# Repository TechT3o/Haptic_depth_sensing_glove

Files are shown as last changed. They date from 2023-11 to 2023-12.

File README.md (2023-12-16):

# Haptic_depth_sensing_glove

Haptic feedback glove device that uses a motor camera and mini motor disks to help visually impaired people understand the 3d space around them.

The idea is to mount a small camera on the palm of the visually impaired user, construct the depth map, and perform sensory substitution of vision by using a high-resolution haptic feedback glove comprised of an array of vibrational mini DC motor disks to assign a different intensity in the direction where the user's hand is pointing at, analogous to how close the object is.

The goal is for the user to be able to identify what type of object their hand is pointing at for object recognition and object fetching and for the user to be able to do wayfinding and navigate in a room using the device.

User studies that examine the usability (Learnability, Efficiency, Memorability, Errors, Satisfaction) and effectiveness of the device will be done.

# Hardware

- 1x [ESP32](https://www.espressif.com/en/products/socs/esp32)
- 1x [OV5640 camera module](https://www.amazon.com/Cameras-2592X1944-Industrial-Windows-Raspberry/dp/B088RD74VC?th=1)
- 20x [Mini motor disk](https://www.adafruit.com/product/1201#technical-details)
- 20x [p2n222A npn transistor](https://www.onsemi.com/pdf/datasheet/p2n2222a-d.pdf)
- 20x 30 Ohms resistor
- 20x 2.2k Ohms resistor
- 20x 33 pF capacitor
- 20x 1N4001 diode
- 20x [motor circuit PCB](https://github.com/TechT3o/Haptic_depth_sensing_glove/tree/main/PCB%20files)

## Motor driver circuit

The mini disk motors require around 100 mA of current in order to rotate at full speed with 5V power. The Arduino output pins can provide up to 10 mA, therefore we need a driver circuit to be able to power the motor using a PWM signal. The circuit shown in Figure 1 was built. It uses an NPN transistor whose base is connected to the GPIO output pin of the Arduino. When the PWM signal gets applied to the base of the transistor the Collector Emitter channel opens and current from the VCC flows through the disk motor and makes it spin with intensity analogous to the PWM signal. The resistor R2 limits the current flowing through the disk motor. A value of 30 Ohms was selected as 5V/30 = 166 mA max current that could flow through R2 ignoring rest of the circuit resistances. R1 was selected to limit the base current. As the base current is very small values of up to 5k could be selected but the chosen value for R1 in this project was 2.2k Ohms. The capacitor is used to soften voltage spikes from the power supply and suppress electrical noise from the motor's rotation and a diode is put to protect against back EMF.



*Figure 1: Motor driver circuit*

The PCB of this circuit shown in Figure 2 was made and the Gerber files were sent to [OSHPARK](https://oshpark.com/) for manufacturing.



*Figure 2: Motor driver PCB*

The received PCBs arrived and the components were soldered on top of it with the disk motors attached to the back of the PCB.



*Figure 3: PCB*



*Figure 4: Soldered circuits and motor coordinates*

## Camera

When choosing the camera we wanted a camera with a small size that could fit the device, as little distortion as possible (no wide angle cameras that tend to have a lot of barrel distortion), low latency and good enough resolution for the depth estimation model to give accurate results. The camera selected was a 5MP USB Camera Webcam with 60 Degree FOV and Autofocus Lens by IFWATER.

It used the OV5640 CMOS (Complementary Metal-Oxide-Semiconductor) image sensor which has high resolution of 2592 x 1944 pixels and can achieve frame rates of 30 FPS.

The location of the camera was another dilemma in our design consideration. As originally intended, it was supposed to be connected to the user's body. However, by relocating the camera to the palm, we eliminated the need to determine the depth relative to the hand, thereby simplifying the entire system. Placing the camera on the palm allows for a more natural interaction with the environment.

## Microcontroller
The microcontroller picked is an ESP32 DevkitC module. It was selected because it is affordable, has the options of wireless connectivity and low power consumption and unlike the Arduino Nano 33 BLE Sense which was the first attempt has no upper limit into how many GPIO pins can provide a PWM signal concurrently. 



*Figure 5: ESP32 module*

## Depth Estimation

In order to estimate the depth from a mono camera the vision transformer model DPT-Large by Intel was used. This transformer was trained on 1.4 million images for monocular depth estimation and it can predict the relative depth in an image frame. The Python class [MonoDepthEstimator](https://github.com/TechT3o/Haptic_depth_sensing_glove/blob/main/depth_estimation.py) implements this transformer with functions that can find the depth of a frame. For sanity checking the depth frames are visualized as a 3D point cloud using the [3D reconstruction](https://github.com/TechT3o/Haptic_depth_sensing_glove/blob/main/3d_reconstruct.py) script and the relative distances between the objects captured seem reasonable and is accurate for which object is closer to the camera. A sample depth video that is used to test the glove in its early stages and to visualize the depth estimation created by the [depth video creating script](https://github.com/TechT3o/Haptic_depth_sensing_glove/blob/main/depth_video_creating_script.py) is shown in Figure 5.



*Figure 6: Mono depth video example*



*Figure 7: Point cloud*

## Intensity mapping

The [IntensityMapper](https://github.com/TechT3o/Haptic_depth_sensing_glove/blob/main/intensity_mapper.py) class is responsible for getting the depth map and the positions of the motors on the glove and getting the PWM values by averaging the values around the corresponding pixel in the depth map. It performs the mapping by being input teh positions of the motors in a coordinate system on the frame of the device.

## Serial Communication

The [serial communicator](https://github.com/TechT3o/Haptic_depth_sensing_glove/blob/main/serial_com.py) class is responnsible for connecting the Python backend serially to the ESP32, transmitting the motor intensities and validating if those intensities were properly received.

## Microcontroller script

The [ESP32 script](https://github.com/TechT3o/Haptic_depth_sensing_glove/blob/main/motor_test.ino) is responsible for listening to the serial communication channel and reading and decoding the comma seperated string message that has the motor itnensities sent by the Python backend. Then it assigns these PWM intensities as PWM signals to the pins corresponding to each motor and send back the received intensities for the backend to confirm whether the communication was correct.

 ## Helper scripts

The [camera calibration](https://github.com/TechT3o/Haptic_depth_sensing_glove/blob/main/calibrate_cam_script.py) script is used to obtain camera parameters such as the foundational matrix, the intrinsic and extrinsic parameters and the lens distortions to be used in the 3D reconstruction or in estimating the depth.

## Prototype

A generic hand shaped frame was formed by gluing together wooden popsickles. Then all the electronics were mounted on top of the frame. The camera and the ESP32 are connected to the laptop through USB ports. The cables controlling the motors are connected to respective digital and analog pins (they both can provide PWM signals) of the ESP32. Lastly the power supply wires are connected to a 5V pwoer supply output and the ground of the power supply and the ESP32 are connected.

By running the [main.py](https://github.com/TechT3o/Haptic_depth_sensing_glove/blob/main/main.py) script we can operate the prototype and a visualziation that shows what the device captures and where the intensity of each motor is found from is shown.



*Figure 6: Prototype*

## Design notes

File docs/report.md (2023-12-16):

# Table of Contents
* Abstract
* [Introduction](#1-introduction)
* [Related Work](#2-related-work)
* [Technical Approach](#3-technical-approach)
* [Evaluation and Results](#4-evaluation-and-results)
* [Discussion and Conclusions](#5-discussion-and-conclusions)
* [References](#6-references)

# Abstract

A Haptic feedback glove device that uses a motor camera and mini motor disks to help visually impaired people understand the 3d space around them.
A small camera is mounted on the palm of a visually impaired user and is used to construct a depth map used to perform sensory substituition of vision using a high resolution haptic feedback device comprised of an array of mini DC motor discs with intensity analogous to how close an object is.
The goal is for the user to be able to do wayfinding and navigate in a room using the device. User studies that examine the usability and quality of the device were done showing that the glove is easy to use, feels intuitive and engaging and is a suitable technique for sensory substitution of vision but was prone to errors, was not efficient and would not be recommended in the current stage to be used as a complete wayfinding solution.

# 1. Introduction

About 284 million people are visually impaired (VI) worldwide and of these, 39 million of them are blind. Common problems that VI people face are the difficulty in navigating / finding their way in the environment, losing objects that are misplaced on surfaces, or identifying and fetching objects around them that are further away from their grasp.

In this project a haptic feedback glove device that uses a motor camera and mini motor disks to help visually impaired people understand the 3D space around them is built. The idea is to mount a small camera on the palm of the visually impaired user, construct the depth map, and perform sensory substitution of vision by using a high-resolution haptic feedback glove comprised of an array of mini DC motor disks to assign a different intensity in the direction where the user's hand is pointing at, analogous to how close the object is. The goal is for the user to be able to identify what type of object their hand is pointing at for object recognition and object fetching and for the user to be able to do wayfinding and navigate in a room using the device.

There are multiple different approaches that have been performed for sensory substitution of vision to aid VI people in performing multiple different tasks and with multiple different technologies. The technologies that rely on audio feedback have the limitations of overloading the sensory channel and are slow to transmit environmental information to the user. Smartphones, tablets, canes, smartwatches, belts, wristbands, and sleeves can transmit a limited amount of information and can't directly provide the 3D space information but require an encoding of this information that is difficult for the user to learn. Resonating pin arrays and sonar arrays require expensive, bulky, and not portable equipment.

Our proposed solution belongs to the family of gloves with motors and aims to tackle the problems of object fetching and wayfinding by allowing for cheap, portable, easy to learn, direct and low-latency feedback of the 3D space without sensory overload. Relative depth information can be extracted from a mono camera using neural networks Sensory substitution can be performed with vibrotactile motor arrays. Shapes, faces and objects can be recognized using motor arrays.
Therefore, it should be feasible to combine this research and construct a haptic depth sensing glove that can perform sensory substitution and explore its effectiveness and usability for the tasks of object fetching and wayfinding.

There are multiple applications for such a device and multiple people can benefit from it. Visually impaired people will now have an alternative to navigate in new environments resulting in greater mobility and quality of life and they will have a way to recognize and fetch objects making them more self-reliant and solving the problem of lost objects. Therefore such a device could practically improve the quality of life of the visually impaired community, let them become more self-reliant, more easily navigate to new places, and alleviate pressure from their caregivers.
With the rise of Virtual Reality headsets and Augmented Reality applications, there is an active research field and a need to develop ubiquitous haptic feedback devices to help a user interact with the virtual world. This glove could be used to address this need and provide haptic feedback such as for button pressing or touching and recognizing virtual objects tasks frequently encountered in Human-Computer Interaction.

Some challenges in the design of this device include:

- Achieving depth estimation with good enough resolution to understand relative distances between camera objects
- Achieving real-time performance so that there is no latency between where the user is pointing and the perceived haptic feedback
- Achieving good enough haptic resolution with the motor array for the user to recognize different objects and perform wayfinding

but with good Python skills to make a running backend that can collect camera information, find the depth, and determine the mapping and intensities of the motors,
with C++ skills to program the ESP32 microcontroller to communicate with the Python backend, and to control the intensities of each motor, with Electronic circuit design and soldering skills to connect the motors and camera to the microcontroller and to create the motor driver circuit and PCBs and with hands-on skills to put the glove together the project is feasible.

A user study was conducted with the goal of evaluating the usability seperated in 5 metrics (Learnability, Efficiency, Memorability, Errors, Satisfaction) of the device for wayfinding by considering quantitative metrics such as the ability of participants to finish the path, the time taken to complete the path and qualitative such as a likert scale questionnaire and recording the comments of the users.

# 2. Related Work

There are multiple different approaches that have been performed for sensory substitution of vision to aid VI people in performing multiple different tasks and with multiple different technologies.

The tasks are:
- Navigating a map
- Wayfinding
- Mental mapping
- VR navigating
- Fetching objects
- Driving
- Feeling 2D data

And the technologies used vary and are:
- Vibrotactile on a mobile device
- Smart walker
- Belt
- Smartphone
- Drone
- VR headset
- Camera Bracelet
- Smart Cane
- Tactile wristband
- Sonar array with vibrotactile motors
- Resonating pin array
- Glove with motors
- Audio feedback
- Tablet
- Sleeve
- Smartwatch

The technologies that rely on audio feedback have the limitations of overloading the sensory channel and are slow to transmit environmental information to the user.
Smartphones, tablets, canes, smartwatches, belts, wristbands, and sleeves can transmit a limited amount of information and can't directly provide the 3D space information but require an encoding of this information that is difficult for the user to learn.
Resonating pin arrays and sonar arrays require expensive, bulky, and not portable equipment.

# 3. Technical Approach

The design of our glove encompasses two fundamental aspects: the hardware and the software

## Hardware

The hardware required for the project involved the camera which was needed to sense the environment as vision is the sense that we want to substitute, the actuator was chosen to be an array of mini vibrational disk motors, the motor driver which was required to operate the disk motors, the microcontroller that was responsible for controlling the disk motor array, the wooden frame that would structure the device and the PC which was the main computational unit.

### Motor array

A motor array was selected to encode the visual information to touch. It was shown that an array of virbtactile motors with enough resolution could be used to understand shapes and therefore it could be used to help BVI understand what kind objects are found around them in space. Vibrating mini motor discs were chosen as they are cheap and small enough to fit in the human palm and can stimulate the pacinian corpuscles (PC) that are the sensory nerve responsible for receiving pressure and vibration that are located in the human palm in high density. 8 motors were placed in the middle of the palm in a square shape and 5 more motors were placed on the finger tips (which have the highest density of PCs) resulting in a 13 motor array.

### Motor driver circuit

From the electronic perspective, the vibrating mini motors that we are using for haptic feedback demand approximately 100 mA of current to achieve optimal rotation at 5V power. Given that the processor’s output pins cannot supply this current, a dedicated driver circuit is essential for powering the motor through a PWM (Pulse Width Modulation) signal. Therefore, we are using NPN transistors with bases connected to the processor pins functioning as a dynamic voltage-controlled current source, to supply the necessary current for motors to work in their optimal operational range. A PWM signal modulates the current supplied to the motors through this configuration, enabling the processor to control the transistors. In addition to meeting the motor's power requirements, this also provides us with haptic feedback because it gives us control over the motor's power.

The mini disk motors require around 100 mA of current in order to rotate at full speed with 5V power. The ESP32 GPIO output pins can provide up to 40 mA, therefore we designed a driver circuit to be able to power the motor using a PWM signal. The circuit shown in Figure 1 was built. It uses an NPN transistor whose base is connected to the GPIO output pin of the ESP32. When the PWM signal gets applied to the base of the transistor the Collector Emitter channel opens and current from the VCC flows through the disk motor and makes it spin with intensity analogous to the PWM signal. The resistor R2 limits the current flowing through the disk motor. A value of 30 Ohms was selected as 5V/30 = 166 mA max current that could flow through R2 ignoring rest of the circuit resistances. R1 was selected to limit the base current. As the base current is very small values of up to 5k could be selected but the chosen value for R1 in this project was 2.2k Ohms. The capacitor is used to soften voltage spikes from the power supply and suppress electrical noise from the motor's rotation and a diode is put to protect against back EMF.



*Figure 1: Motor driver circuit*

The PCB of this circuit shown in Figure 2 was made and the Gerber files were sent to [OSHPARK](https://oshpark.com/) for manufacturing.



*Figure 2: Motor driver PCB*

The received PCBs arrived and the components were soldered on top of it with the disk motors attached to the back of the PCB.



*Figure 3: PCB*



*Figure 4: Soldered circuits*

### Camera

When choosing the camera we wanted a camera with a small size that could fit the device, as little distortion as possible (no wide angle cameras that tend to have a lot of barrel distortion), low latency and good enough resolution for the depth estimation model to give accurate results. The camera selected was a 5MP USB Camera Webcam with 60 Degree FOV and Autofocus Lens by IFWATER.

It used the OV5640 CMOS (Complementary Metal-Oxide-Semiconductor) image sensor which has high resolution of 2592 x 1944 pixels and can achieve frame rates of 30 FPS.

The location of the camera was another dilemma in our design consideration. As originally intended, it was supposed to be connected to the user's body. However, by relocating the camera to the palm, we eliminated the need to determine the depth relative to the hand, thereby simplifying the entire system. Placing the camera on the palm allows for a more natural interaction with the environment.

### Microcontroller
The microcontroller picked is an ESP32 DevkitC module. It was selected because it is affordable, has the options of wireless connectivity and low power consumption and unlike the Arduino Nano 33 BLE Sense which was the first attempt has no upper limit into how many GPIO pins can provide a PWM signal concurrently. 



*Figure 5: ESP32 module*

### Frame

In order to structure the device and mount these electronics a frame was created by gluing wooden popsickles together into the hand like structure. A whole was cut in the middle in order for the wires to pass through and then the motor modules and the camera were hot glued on the wooden skeleton. A rubber band was also hot glued in order to be able to attach the device on the user creating the prototype shown in Figure 6.



*Figure 6: Prototype*

### Computational Unit (PC)

For running the backend and perform the most computationally intensive parts we used an HP Pavilion gaming laptop with an AMD Ryzen 7 5800H CPU and an NVIDIA GeForce RTX 3050 Laptop GPU.

## Software
The software side consisted of the depth estimation algorithm, the serial communication and mapping the depth to the intensity of the motor.

### Depth Estimation

In order to estimate the depth from a mono camera the vision transformer model DPT-Large by Intel was used. This transformer was trained on 1.4 million images for monocular depth estimation and it can predict the relative depth in an image frame. DPT uses the Vision Transformer (ViT) as backbone and adds a neck + head on top for monocular depth estimation.

A depth video produced with this model is shown in Figure 7. For this particular application the relative depth works well as we want to make sure that the user can understand which object is closer to them to avoid collision and we are not as interested in the absolute depth value. By reconstructing the point cloud of a depth frame in Figure 8 we see that the scales captured are sensible.

The depth estimation is the bottleneck of this pipeline with inferences taking approximately 160ms when operating in our computing unit and it's performance reduces in challenging or low light conditions.



*Figure 7: Mono depth video example*



*Figure 8: Point cloud*

### Intensity mapping

We investigated a mapping technique in order to translate the visual depth information into a PWM value that will control the intensity of the motor. The locations of the motors in a device surface coordinate system is given and is projected on the dimensions of the depth map. Then a window is taken around each pixel value and the average of the depth values is found to avoid extreme erroneous depth values that may result by considering a single pixel. As the motors start to operate with a PWM signal above 70 / 255, objects that are very far away do not make the motors vibrate which is beneficial as we do not want the sensory channel to get oversaturated.

### Serial Communication

A serial communication of 9600 baud rate is formed between the Python backend that captures the image, finds the depth, maps the intensity and transmits it and the ESP32 that can send feedback that the communication is succesfull as well as if the motors are in operation. 

## Pototype device

With this we have the prototype device. It works by:
- uploading .ino code to ESP32
- Connecting the ESP32 serially to a USB port of the PC
- Connecting the camera to another USB port of the PC
- Connecting the glove to a power supply
- Conencting the GND of the ESP32 to the glove's power supply
- Running the main.py of the Python backend

This prototype was used for the user study but had limitations such as the length of the USB cables and the power supply cable. Future work should investigate a wireless design that would not require the PC to be dragged along the subject.

# 4. Evaluation and Results

In order to evaluate the usability of the glove a user study was performed on 5 not blind or visually impaired users and qualitative and quantitative feedback was gathered. We measure usability by seperating it into five qualitative metrics Learnability, Efficiency, Memorability, Errors and Satisfaction. A picture of the setup of the user study is shown in Figure 9.



*Figure 9: User study setup*

The study consisted of the physical test where participants had to walk the corridor of engineering 4 UCLA building blindfolded in order to test the sensory substitution ability of the device. The path started inside the graduate lounge where the participants had to find the door and exit the room. Then the participants had to move toward the corner and then proceed to the first corridor. The participants then had to walk down the corridor for 10 m where the end of the path was. This path is shown on Figure 10. 



*Figure 10: Navigation path*

The time taken to get to the finish line as well as the number of errors (collisions) was recorded and is shown in Table 1.



*Table 1: Path completion times and number of errors / collision*

After completing the path the users were given a likert scale questionnaire. The questionnaire is shown in Appendix 1 and had the questions seperated into these five different metrics with 2 for Learnability, 4 for Efficiency, 3 for Memorability, 2 for Errors and 4 for Satisfaction. The mean values for each question are found in Table 2 and the box plots of the responses of each participant for every metric is shown in Figure 11. 



*Table 2: Questionnaire mean value answers for each question*



*Figure 11: Questionnaire results box plots for different metrics*

Observing the comments of the participants while performing the physical task we recorded comments such as "This feels cool", "Interesting", "I can't understand where the object is" and "I can't move my hand without pulling the cables".

# 5. Discussion and Conclusions

## Discussion

The user study gave insights about the usability of the device at the current prototype stage.

Concerning the wayfinding efficiency we see that the time taken for the participants to complete the path had a mean of 75.4 seconds (compared to approximately 12 seconds with sense of vision) and standard deviation of 6.7 and the number of errors was 4.4 errors with standard deviation 1.51. We see that the standard deviations of the time and errors are small that shows consistency accross participants and indicates that the learnability of the device was similar between subjects. We see that all participants have at least 3 errors so there is a learning curve in learning to operate the device. The fact that all participants completed the wayfinding path shows the potential of this device to perform sensory substitution for the task of navigating in a closed space. It is worth to be noted that the participants probably already had a mental model of the building so it might have been easier to navigate compared to being subjected to a completely usneen environment. Getting access to one of the relevant devices discussed in section 2 or a white cane to have a comparison metric would be of interest.

Analyzing the results of the questionnaire by drawing box plots for the different usability metrics we can see that the learnability of this device rates the highest as the time and error metrics also suggested and shows that this type of sensory substitution feels intuitive for the users. The second highest metric is memorability that shows that the user's felt confident reusing or teaching other people how to use the device. This gives insight that the device is considered simple to use. Then the Errors, Satisfaction and Efficiency metrics average around the value of 4 which is a neutral stance with small deviation from the median value showing that all users agreed that the device was not satisfactory, not efficient and had errors. By inspecting the answers in Table 2 for these 3 metrics we see that concerning the error there were many difficulties when using the device but it was easy to recover from these mistakes. Concerning Satisfaction they found the activity engaging but would not use this device for wayfinding. And concerning efficiency they found the device easy to use but they couldn't effectively perform wayfinding.

Combining the qualitative feedback we see that we have positive comments such as "This feels cool" and "Interesting" but also negative comments such as "I can't understand where the object is" and "I can't move my hand without pulling the cables" that agrees with the satisfaction, errors and efficiency metrics being in the middle of the likert scale.

Analyzing this feedback it is understandable that a wireless version of the glove that does not use a power cord that obstructs the movement of the users should be used as this would allow for the users to move without having somebody drag a chair with the circuits and computational unit connected along them hindering their speed and range of motion. Also the resolution of the motor array was not enough to understand the shape of the object the device was pointing at so increasing the resolution is also a future step. In the user study, the participants were UCLA students that might have been familiar with the layout of the Engineering IV building and have already had developed a mental model of the path making the result of the path unreliable. Other future work should include user studies with more participants participants that follow a path in a completely new and unseen envronment, they should ideally be visually impaired in order to get more representative feedback and a baseline such as the other approaches mentioned in Section 2 or a white cane should be used to compare our approach.

## Conclusion

A functional real time operating prototype device that combined the software and hardware parts to perform sensory substitution of vision into haptic feedback was developed. Then the results of the user study concluded that the device could be used to perform sensory substitution and was easy to use but did not have enough resolution to udnerstand the shape of the objects and was deemed as unsatisfactoy, inefficient and error prone for the task of wayfinding. Future work includes optimizing the prototype with the feedback collected (e.g. making it wireless) and conducting a larger scale user study with visually impaired people while having a baseline sensory substitution method for comparison.

# 6. References

[1]Yatani, K., Banovic, N., & Truong, K. (2012, May). SpaceSense: representing geographical information to visually impaired people using spatial tactile feedback. In Proceedings of the SIGCHI Conference on Human Factors in Computing Systems (pp. 415-424).

[2] Jimenez, M. F., Mello, R. C., Bastos, T., & Frizera, A. (2020). Assistive locomotion device with haptic feedback for guiding visually impaired people. Medical Engineering & Physics, 80, 18-25.

[3] Katzschmann, R. K., Araki, B., & Rus, D. (2018). Safe local navigation for visually impaired users with a time-of-flight and haptic feedback device. IEEE Transactions on Neural Systems and Rehabilitation Engineering, 26(3), 583-593.

[4] Fagernes, S., & Grønli, T. M. (2018). Navigation for visually impaired using haptic feedback. In Human-Computer Interaction. Interaction in Context: 20th International Conference, HCI International 2018, Las Vegas, NV, USA, July 15–20, 2018, Proceedings, Part II 20 (pp. 347-356). Springer International Publishing.

[5] Huppert, F., Hoelzl, G., & Kranz, M. (2021, May). GuideCopter-A precise drone-based haptic guidance interface for blind or visually impaired people. In Proceedings of the 2021 CHI Conference on Human Factors in Computing Systems (pp. 1-14).

[6] Lahav, O., & Mioduser, D. (2008). Haptic-feedback support for cognitive mapping of unknown spaces by people who are blind. International Journal of Human-Computer Studies, 66(1), 23-35.

[7] Moustakas, K., Nikolakis, G., Kostopoulos, K., Tzovaras, D., & Strintzis, M. G. (2007). Haptic rendering of visual data for the visually impaired. IEEE MultiMedia, 14(1), 62-72.

[8] Scheggi, S., Talarico, A., & Prattichizzo, D. (2014, June). A remote guidance system for blind and visually impaired people via vibrotactile haptic feedback. In 22nd Mediterranean conference on control and automation (pp. 20-23). IEEE.

[9] Zhang, X., Zhang, H., Zhang, L., Zhu, Y., & Hu, F. (2019). Double-diamond model-based orientation guidance in wearable human–machine navigation systems for blind and visually impaired people. Sensors, 19(21), 4670.

[10] Kuriakose, B., Shrestha, R., & Sandnes, F. E. (2020, July). Smartphone navigation support for blind and visually impaired people-a comprehensive analysis of potentials and opportunities. In Universal Access in Human-Computer Interaction. Applications and Practice: 14th International Conference, UAHCI 2020, Held as Part of the 22nd HCI International Conference, HCII 2020, Copenhagen, Denmark, July 19–24, 2020, Proceedings, Part II (pp. 568-583). Cham: Springer International Publishing.

[11] Cardin, S., Thalmann, D., & Vexo, F. (2007). A wearable system for mobility improvement of visually impaired people. The Visual Computer, 23, 109-118.

[12] Ramirez, A. R. G., da Silva, R. F. L., Cinelli, M. J., & de Albornoz, A. D. C. (2012). Evaluation of electronic haptic device for blind and visually impaired people: a case study. Journal of Medical and Biological Engineering, 32(6), 423-428.

[13] He, L., Wang, R., & Xu, X. (2020, April). PneuFetch: supporting blind and visually impaired people to fetch nearby objects via light haptic cues. In Extended Abstracts of the 2020 CHI Conference on Human Factors in Computing Systems (pp. 1-9).

[14] Pokluda, L., & Sochor, J. (2003). Spatial haptic orientation for visually impaired people. EG, 3, 29-34.

[15] Wi, D., Sodemann, A., & Chicci, R. (2017, August). Vibratory haptic feedback assistive device for visually-impaired drivers. In 2017 IEEE SmartWorld, Ubiquitous Intelligence & Computing, Advanced & Trusted Computed, Scalable Computing & Communications, Cloud & Big Data Computing, Internet of People and Smart City Innovation (SmartWorld/SCALCOM/UIC/ATC/CBDCom/IOP/SCI) (pp. 1-5). IEEE.

[16] Poggi, M., & Mattoccia, S. (2016, June). A wearable mobility aid for the visually impaired based on embedded 3D vision and deep learning. In 2016 IEEE symposium on computers and communication (ISCC) (pp. 208-213). IEEE.

[17] Xiao, J., Joseph, S. L., Zhang, X., Li, B., Li, X., & Zhang, J. (2015). An assistive navigation framework for the visually impaired. IEEE transactions on human-machine systems, 45(5), 635-640.

[18] Treuillet, S., Royer, E., Chateau, T., Dhome, M., & Lavest, J. M. (2007, August). Body Mounted Vision System for Visually Impaired Outdoor and Indoor Wayfinding Assistance. In CVHI.

[19] Kulyukin, V., Gharpure, C., Nicholson, J., & Osborne, G. (2006). Robot-assisted wayfinding for the visually impaired in structured indoor environments. Autonomous robots, 21, 29-41.

[20] Zhang, H., & Ye, C. (2016, December). An indoor navigation aid for the visually impaired. In 2016 IEEE international conference on robotics and biomimetics (ROBIO) (pp. 467-472). IEEE.

[21] Yang, G., & Saniie, J. (2020). Sight-to-sound human-machine interface for guiding and navigating visually impaired people. IEEE Access, 8, 185416-185428.

[22] Zöllner, M., Huber, S., Jetter, H. C., & Reiterer, H. (2011). NAVI–a proof-of-concept of a mobile navigational aid for visually impaired based on the microsoft kinect. In Human-Computer Interaction–INTERACT 2011: 13th IFIP TC 13 International Conference, Lisbon, Portugal, September 5-9, 2011, Proceedings, Part IV 13 (pp. 584-587). Springer Berlin Heidelberg.

[23] Kammoun, S., Parseihian, G., Gutierrez, O., Brilhault, A., Serpa, A., Raynal, M., ... & Jouffrais, C. (2012). Navigation and space perception assistance for the visually impaired: The NAVIG project. Irbm, 33(2), 182-189.

[24] Bai, J., Liu, Z., Lin, Y., Li, Y., Lian, S., & Liu, D. (2019). Wearable travel aid for environment perception and navigation of visually impaired people. Electronics, 8(6), 697.

[25] Li, B., Munoz, J. P., Rong, X., Chen, Q., Xiao, J., Tian, Y., ... & Yousuf, M. (2018). Vision-based mobile indoor assistive navigation aid for blind people. IEEE transactions on mobile computing, 18(3), 702-714.

[26] Gay, S. L., Pissaloux, E., Romeo, K., & Truong, N. T. (2021). F2T: a novel force-feedback haptic architecture delivering 2D data to visually impaired people. IEEE Access, 9, 94901-94911.

[27] Zahn, M., & Khan, A. A. (2022). Obstacle avoidance for blind people using a 3D camera and a haptic feedback sleeve. arXiv preprint arXiv:2201.04453.

[28] Zelek, J. S., Bromley, S., Asmar, D., & Thompson, D. (2003). A haptic glove as a tactile-vision sensory substitution for wayfinding. Journal of Visual Impairment & Blindness, 97(10), 621-632.

[29] Shrewsbury, B. T. (2011, October). Providing haptic feedback using the kinect. In The proceedings of the 13th international ACM SIGACCESS conference on Computers and accessibility (pp. 321-322).

[30] Shen, H., Edwards, O., Miele, J., & Coughlan, J. M. (2013, October). CamIO: a 3D computer vision system enabling audio/haptic interaction with physical objects by blind users. In Proceedings of the 15th International ACM SIGACCESS Conference on Computers and Accessibility (pp. 1-2).

[31] Bauer, Z., Dominguez, A., Cruz, E., Gomez-Donoso, F., Orts-Escolano, S., & Cazorla, M. (2020). Enhancing perception for the visually impaired with deep learning techniques and low-cost wearable sensors. Pattern recognition letters, 137, 27-36.

[32] Yelamarthi, K., DeJong, B. P., & Laubhan, K. (2014, August). A kinect based vibrotactile feedback system to assist the visually impaired. In 2014 IEEE 57th International Midwest Symposium on Circuits and Systems (MWSCAS) (pp. 635-638). IEEE.

[33] Kaczmarek, K. A., Webster, J. G., Bach-y-Rita, P., & Tompkins, W. J. (1991). Electrotactile and vibrotactile displays for sensory substitution systems. IEEE transactions on biomedical engineering, 38(1), 1-16.

[34] Ribani, R., & Marengoni, M. (2019, January). Vision Substitution with Object Detection and Vibrotactile Stimulus. In VISIGRAPP (4: VISAPP) (pp. 584-590).

[35] Bach-y-Rita, P., & Kercel, S. W. (2003). Sensory substitution and the human–machine interface. Trends in cognitive sciences, 7(12), 541-546.

[36] Mante, N., & Weiland, J. D. (2018, July). Visually impaired users can locate and grasp objects under the guidance of computer vision and non-visual feedback. In 2018 40th Annual International Conference of the IEEE Engineering in Medicine and Biology Society (EMBC) (pp. 1-4). IEEE.

[37] Alahakone, A. U., & Senanayake, S. A. (2009, July). Vibrotactile feedback systems: Current trends in rehabilitation, sports and information display. In 2009 IEEE/ASME International Conference on Advanced Intelligent Mechatronics (pp. 1148-1153). IEEE.

[38] Bastidas Cuya, F. G., Martins Guarese, R. L., Johansson, C. G., Giambastiani, M., Iquiapaza, Y., de Jesus Oliveira, V. A., ... & Maciel, A. (2021, October). Vibrotactile Data Physicalization: Exploratory Insights for Haptization of Low-resolution Images. In Symposium on Virtual and Augmented Reality (pp. 84-91).

[39] Intel DPT-Large Mono depth estimator

[40] Eagle EDA

# Appendix 1

[depth_glove_form.pdf](https://github.com/TechT3o/Haptic_depth_sensing_glove/files/13643433/depth_glove_form.pdf)

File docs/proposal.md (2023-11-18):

# Project Proposal

## 1. Motivation & Objective

About 284 million people are visually impaired (VI) worldwide and of these, 39 million of them are blind. Common problems that VI people face are the difficulty in navigating / finding their way in the environment, losing objects that are misplaced on surfaces, or identifying and fetching objects around them that are further away from their grasp.

In this project a haptic feedback glove device that uses a motor camera and mini motor disks to help visually impaired people understand the 3D space around them is built. The idea is to mount a small camera on the palm of the visually impaired user, construct the depth map, and perform sensory substitution of vision by using a high-resolution haptic feedback glove comprised of an array of mini DC motor disks to assign a different intensity in the direction where the user's hand is pointing at, analogous to how close the object is.

The goal is for the user to be able to identify what type of object their hand is pointing at for object recognition and object fetching and for the user to be able to do wayfinding and navigate in a room using the device. User studies that examine the usability and effectiveness of the device will be done.

## 2. State of the Art & Its Limitations

There are multiple different approaches that have been performed for sensory substitution of vision to aid VI people in performing multiple different tasks and with multiple different technologies.

The tasks are:
- Navigating a map
- Wayfinding
- Mental mapping
- VR navigating
- Fetching objects
- Driving
- Feeling 2D data

And the technologies used vary and are:
- Vibrotactile on a mobile device
- Smart walker
- Belt
- Smartphone
- Drone
- VR headset
- Camera Bracelet
- Smart Cane
- Tactile wristband
- Sonar array with vibrotactile motors
- Resonating pin array
- Glove with motors
- Audio feedback
- Tablet
- Sleeve
- Smartwatch

The technologies that rely on audio feedback have the limitations of overloading the sensory channel and are slow to transmit environmental information to the user.
Smartphones, tablets, canes, smartwatches, belts, wristbands, and sleeves can transmit a limited amount of information and can't directly provide the 3D space information but require an encoding of this information that is difficult for the user to learn.
Resonating pin arrays and sonar arrays require expensive, bulky, and not portable equipment.

## 3. Novelty & Rationale

Our proposed solution belongs to the family of gloves with motors and aims to tackle the problems of object fetching and wayfinding by allowing for cheap, portable, easy to learn, direct and low-latency feedback of the 3D space without sensory overload.

The resources indicate that:
- Relative depth information can be extracted from a mono camera using neural networks
- Sensory substitution can be performed with vibrotactile motor arrays
- Shapes, faces and objects can be recognized using motor arrays.

Therefore, it should be feasible to combine this research and construct a haptic depth sensing glove that can perform sensory substitution and explore its effectiveness and usability for the tasks of object fetching and wayfinding.

## 4. Potential Impact

### Technical Impact

The technologies developed for this project will have a technical impact since:
- A haptic feedback device will be developed
- The sensitivity and resolution of the human palm to vibrotactile feedback will be investigated
- A real-time mono camera depth estimation system that can be used by embedded devices will be developed

  ### Broad impact

  There are multiple applications for such a device and multiple people can benefit from it.
  
  Visually impaired people will now:
  - have an alternative to navigate in new environments resulting in greater mobility and quality of life.
  - have a way to recognize and fetch objects making them more self-reliant and solving the problem of lost objects.

  Therefore such a device could practically improve the quality of life of the visually impaired community, let them become more self-reliant, more easily navigate to new places, and alleviate pressure from their caregivers.

   With the rise of Virtual Reality headsets and Augmented Reality applications, there is an active research field and a need to develop ubiquitous haptic feedback devices to help a user interact with the virtual world. This glove could be used to address this need and provide haptic feedback such as for button pressing or touching and recognizing virtual objects tasks frequently encountered in Human-Computer Interaction.

## 5. Challenges

- Achieving depth estimation with good enough resolution to understand relative distances between camera objects
- Achieve real-time performance so that there is no latency between where the user is pointing and the perceived haptic feedback
- Achieve good enough haptic resolution with the motor array for the user to recognize different objects and perform wayfinding

## 6. Requirements for Success

- Python skills are required to make a running backend that can collect camera information, find the depth, and determine the mapping and intensities of the motors.
- C++ skills are needed to program the Arduino to communicate with the Python backend, and to control the intensities of each motor.
- Electronic circuit design and soldering skills are required to connect the motors and camera to the microcontroller and to create the motor driver circuit and PCBs.
- 3D printing and design skills are required to print casing for electronic components.
- Hands-on skills are required to put the glove together.

## 7. Metrics of Success

### Quantitative

#### Wayfinding / navigation study
Navigation accuracy - Able to navigate in the room?
Navigation speed - How much time to reach the destination?

#### Object recognition / fetching study
Recognition accuracy - How many objects were detected? 
Recognition speed - How much time to figure out an object?

### Qualitative
- Interview (record answers and do affinity diagram)
- Likert scale questionnaires to figure usability

#### Usability
- Learnability
- Efficiency
- Memorability
- Errors
- Satisfaction

## 8. Execution Plan

### Glove / Haptic side

- Design motor driver circuit.
- Design motor pcb.
- Assemble motor PCBs.
- Check which array configuration is best ( How many motors are in an array, in which places to be placed, what kind of depth to intensity mapping).
- Check if it is possible to understand the type of object using the sensor array. (we can use depth maps from other sources as well for testing this).
- Figure depth resolution ( Can you understand two objects being n meters apart from each other).
(These might all change depending on depth to intensity mapping, the position of motors etc)

### Camera side

- Find which camera to use.
- Find where/ how it is convenient to place the camera.
- Transmit camera data to PC.
- Optimize depth estimation pipeline (model, processing, depth to motor intensity conversion etc) to run in real time. (What is the effect of different estimations per second on perceived accuracy?).

### Combine the two

- 3D print cases / parts for mounting electronic components.
- Assemble the glove.
- Transmit data serially (or wirelessly) between the processing backend and haptic glove.
- Start user testing.

### Extension:

- Make glove wireless.
- Make glove battery-powered.
- Try 3d reconstruction of space and handling VR objects

## 9. Related Work

### 9.a. Papers

- SpaceSense: representing geographical information to visually impaired people using spatial tactile feedback.

Related since it uses tactile feedback to transfer digital information to VI people.

- Assistive locomotion device with haptic feedback for guiding visually impaired people.

Another type of haptic feedback device is used for wayfinding of VI people.

- Safe local navigation for visually impaired users with a time-of-flight and haptic feedback device.

Similar concept but uses the time of flight sensor and doesn't use a motor array.

- Navigation for the visually impaired using haptic feedback.

Also explores using haptic feedback to transfer location information.

- GuideCopter-A precise drone-based haptic guidance interface for blind or visually impaired people.

Different haptic feedback techniques for guiding VI people.

- Haptic-feedback support for cognitive mapping of unknown spaces by people who are blind.

Present haptic feedback and the idea of mental mapping for blind people that is a potential application of our proposed solution 

- Haptic rendering of visual data for the visually impaired.

Related since it uses tactile feedback to transfer digital information to VI people.

- A remote guidance system for blind and visually impaired people via vibrotactile haptic feedback.

Also explores using vibrotactile haptic feedback to guide VI people.

- Double-diamond model-based orientation guidance in wearable human–machine navigation systems for blind and visually impaired people.

Explains other types of HCI for orientation guidance of VI people.

- Smartphone navigation support for blind and visually impaired people-a comprehensive analysis of potentials and opportunities.

Other types of navigation devices for VI people.

- A wearable system for mobility improvement of visually impaired people.

Similar kind of system improves the mobility of VI people.

- Evaluation of electronic haptic device for blind and visually impaired people: a case study.

Summary paper explaining many uses of haptic devices to aid VI people.

- PneuFetch: supporting blind and visually impaired people to fetch nearby objects via light haptic cues.

A different approach to object fetching for VI people.

- Spatial haptic orientation for visually impaired people.

Similar approach of using haptic feedback for orientation for VI people.

- Vibratory haptic feedback assistive device for visually-impaired drivers.

Haptic feedback method for VI people even though the addressed problem is driving

- A wearable mobility aid for the visually impaired based on embedded 3D vision and deep learning.

Similar to the concept of finding depth map with embedded devices even though different device type

- An assistive navigation framework for the visually impaired.

Other types of navigation for visually impaired people

- Body Mounted Vision System for Visually Impaired Outdoor and Indoor Wayfinding Assistance.

Other approaches of wayfinding using body mounted components for VI people.

- Robot-assisted wayfinding for the visually impaired in structured indoor environments.

Other approaches of wayfinding for VI people.

- An indoor navigation aid for the visually impaired.

Other types of navigation approach for VI people.

- Sight-to-sound human-machine interface for guiding and navigating visually impaired people.

Other types of sensory substitution systems for aiding VI people.

- NAVI–a proof-of-concept of a mobile navigational aid for the visually impaired based on the Microsoft Kinect.

Other types of using depth cameras for the navigation of VI people.

- Navigation and space perception assistance for the visually impaired: The NAVIG project.

Similar in the way that it explores navigation in space for VI people.

- Wearable travel aid for environment perception and navigation of visually impaired people.

Similar problems are solved with different types of devices.

- Vision-based mobile indoor assistive navigation aid for blind people.

Another use of vision for navigation for VI people.

- F2T: a novel force-feedback haptic architecture delivering 2D data to visually impaired people.

Related since it uses tactile feedback to transfer digital information to VI people.

- Obstacle avoidance for blind people using a 3D camera and a haptic feedback sleeve.

Similar concept but it uses a sleeve instead of a glove.

- A haptic glove as a tactile-vision sensory substitution for wayfinding.

Very similar paper as they also use a glove-based embedded system to do sensory substitution for wayfinding.

- Providing haptic feedback using the Kinect.

Similar in that they use 3d maps and haptic feedback.

- CamIO: a 3D computer vision system enabling audio/haptic interaction with physical objects by blind users.

Related to the extension of the project for VR applications, but the technology vision and haptic part of technology are similar.

- Enhancing perception for the visually impaired with deep learning techniques and low-cost wearable sensors.

Similar idea of using deep learning vision and low-cost wearable sensors.

- A Kinect-based vibrotactile feedback system to assist the visually impaired.

Similar project where they use depth map to provide tactile feedback.

- Electrotactile and vibrotactile displays for sensory substitution systems.

Checks the effectiveness of a vibrotactile display (similar to a motor array) for sensory substitution. 

- Vision Substitution with Object Detection and Vibrotactile Stimulus.

Checks vision substitution system with vibrotactile motors.

- Sensory substitution and the human–machine interface.

Summary of sensory substitution in HCI.

- Visually impaired users can locate and grasp objects under the guidance of computer vision and non-visual feedback.

Similar concept of recognizing and fetching objects using computer vision. Different types of stimulus such as audio and tactile explored.

- Vibrotactile feedback systems: Current trends in rehabilitation, sports, and information display.

Summary of uses of vibrotactile feedback systems.

- Vibrotactile Data Physicalization: Exploratory Insights for Haptization of Low-resolution Images.

Gives insights on understanding low-resolution images using vibrotactile motors.

### 9.b. Datasets

List datasets that you have identified and plan to use. Provide references (with full citation in the References section below).

### 9.c. Software

Intel DPT-Large mono depth sensing model

Eagle EDA

## 10. References

[[1](https://www.researchgate.net/publication/254005210_SpaceSense_Representing_Geographical_Information_to_Visually_Impaired_People_Using_Spatial_Tactile_Feedback)]Yatani, K., Banovic, N., & Truong, K. (2012, May). SpaceSense: representing geographical information to visually impaired people using spatial tactile feedback. In Proceedings of the SIGCHI Conference on Human Factors in Computing Systems (pp. 415-424).

[[2](https://pubmed.ncbi.nlm.nih.gov/32446757/)] Jimenez, M. F., Mello, R. C., Bastos, T., & Frizera, A. (2020). Assistive locomotion device with haptic feedback for guiding visually impaired people. Medical Engineering & Physics, 80, 18-25.

[[3](https://dspace.mit.edu/bitstream/handle/1721.1/114285/Katzschmann%20et%20al.%20-%202018%20-%20Safe%20Local%20Navigation%20for%20Visually%20Impaired%20Users%20with%20a%20Time-of-Flight%20and%20Haptic%20Feedback%20Device%20-%20Final.pdf)]  Katzschmann, R. K., Araki, B., & Rus, D. (2018). Safe local navigation for visually impaired users with a time-of-flight and haptic feedback device. IEEE Transactions on Neural Systems and Rehabilitation Engineering, 26(3), 583-593.

[[4](https://www.researchgate.net/publication/325468302_Navigation_for_Visually_Impaired_Using_Haptic_Feedback)] Fagernes, S., & Grønli, T. M. (2018). Navigation for visually impaired using haptic feedback. In Human-Computer Interaction. Interaction in Context: 20th International Conference, HCI International 2018, Las Vegas, NV, USA, July 15–20, 2018, Proceedings, Part II 20 (pp. 347-356). Springer International Publishing.

[[5](https://dl.acm.org/doi/10.1145/3411764.3445676)] Huppert, F., Hoelzl, G., & Kranz, M. (2021, May). GuideCopter-A precise drone-based haptic guidance interface for blind or visually impaired people. In Proceedings of the 2021 CHI Conference on Human Factors in Computing Systems (pp. 1-14).

[[6](https://www.sciencedirect.com/science/article/pii/S1071581907001012)] Lahav, O., & Mioduser, D. (2008). Haptic-feedback support for cognitive mapping of unknown spaces by people who are blind. International Journal of Human-Computer Studies, 66(1), 23-35.

[[7](https://www.researchgate.net/publication/3338948_Haptic_Rendering_of_Visual_Data_for_the_Visually_Impaired)] Moustakas, K., Nikolakis, G., Kostopoulos, K., Tzovaras, D., & Strintzis, M. G. (2007). Haptic rendering of visual data for the visually impaired. IEEE MultiMedia, 14(1), 62-72.

[[8](https://www.researchgate.net/publication/263195992_A_remote_guidance_system_for_blind_and_visually_impaired_people_via_vibrotactile_haptic_feedback)] Scheggi, S., Talarico, A., & Prattichizzo, D. (2014, June). A remote guidance system for blind and visually impaired people via vibrotactile haptic feedback. In 22nd Mediterranean conference on control and automation (pp. 20-23). IEEE.

[[9](https://pubmed.ncbi.nlm.nih.gov/31661798/)] Zhang, X., Zhang, H., Zhang, L., Zhu, Y., & Hu, F. (2019). Double-diamond model-based orientation guidance in wearable human–machine navigation systems for blind and visually impaired people. Sensors, 19(21), 4670.

[[10](https://www.researchgate.net/publication/342835249_Smartphone_Navigation_Support_for_Blind_and_Visually_Impaired_People_-_A_Comprehensive_Analysis_of_Potentials_and_Opportunities)] Kuriakose, B., Shrestha, R., & Sandnes, F. E. (2020, July). Smartphone navigation support for blind and visually impaired people-a comprehensive analysis of potentials and opportunities. In Universal Access in Human-Computer Interaction. Applications and Practice: 14th International Conference, UAHCI 2020, Held as Part of the 22nd HCI International Conference, HCII 2020, Copenhagen, Denmark, July 19–24, 2020, Proceedings, Part II (pp. 568-583). Cham: Springer International Publishing.

[[11](https://link.springer.com/article/10.1007/s00371-006-0032-4)] Cardin, S., Thalmann, D., & Vexo, F. (2007). A wearable system for mobility improvement of visually impaired people. The Visual Computer, 23, 109-118.

[[12](https://staff.www.ltu.se/~kalevi/References/Evaluation%20of%20electronic%20haptic%20device%20for%20blind%20and%20visually%20impaired%20people%20A%20case%20study.pdf)] Ramirez, A. R. G., da Silva, R. F. L., Cinelli, M. J., & de Albornoz, A. D. C. (2012). Evaluation of electronic haptic device for blind and visually impaired people: a case study. Journal of Medical and Biological Engineering, 32(6), 423-428.

[[13](https://makeabilitylab.cs.washington.edu/media/publications/He_PneufetchSupportingBlindAndVisuallyImpairedPeopleToFetchNearbyObjectsViaLightHapticCues_CHI2020.pdf)] He, L., Wang, R., & Xu, X. (2020, April). PneuFetch: supporting blind and visually impaired people to fetch nearby objects via light haptic cues. In Extended Abstracts of the 2020 CHI Conference on Human Factors in Computing Systems (pp. 1-9).

[[14](https://decibel.fi.muni.cz/download/papers/pokluda03.pdf)] Pokluda, L., & Sochor, J. (2003). Spatial haptic orientation for visually impaired people. EG, 3, 29-34.

[[15](https://www.researchgate.net/publication/326050483_Vibratory_Haptic_feedback_assistive_device_for_visually-impaired_drivers)] Wi, D., Sodemann, A., & Chicci, R. (2017, August). Vibratory haptic feedback assistive device for visually-impaired drivers. In 2017 IEEE SmartWorld, Ubiquitous Intelligence & Computing, Advanced & Trusted Computed, Scalable Computing & Communications, Cloud & Big Data Computing, Internet of People and Smart City Innovation (SmartWorld/SCALCOM/UIC/ATC/CBDCom/IOP/SCI) (pp. 1-5). IEEE.

[[16](https://ieeexplore.ieee.org/stamp/stamp.jsp?tp=&arnumber=7543741&tag=1)] Poggi, M., & Mattoccia, S. (2016, June). A wearable mobility aid for the visually impaired based on embedded 3D vision and deep learning. In 2016 IEEE symposium on computers and communication (ISCC) (pp. 208-213). IEEE.

[[17](https://ieeexplore.ieee.org/stamp/stamp.jsp?tp=&arnumber=7010003)] Xiao, J., Joseph, S. L., Zhang, X., Li, B., Li, X., & Zhang, J. (2015). An assistive navigation framework for the visually impaired. IEEE transactions on human-machine systems, 45(5), 635-640.

[[18](https://www.researchgate.net/publication/221311676_Body_Mounted_Vision_System_For_Visually_Impaired_Outdoor_And_Indoor_Wayfindind_Assistance)] Treuillet, S., Royer, E., Chateau, T., Dhome, M., & Lavest, J. M. (2007, August). Body Mounted Vision System for Visually Impaired Outdoor and Indoor Wayfinding Assistance. In CVHI.

[[19](https://link.springer.com/article/10.1007/s10514-006-7223-8)] Kulyukin, V., Gharpure, C., Nicholson, J., & Osborne, G. (2006). Robot-assisted wayfinding for the visually impaired in structured indoor environments. Autonomous robots, 21, 29-41.

[[20](https://dl.acm.org/doi/abs/10.1109/ROBIO.2016.7866366)] Zhang, H., & Ye, C. (2016, December). An indoor navigation aid for the visually impaired. In 2016 IEEE international conference on robotics and biomimetics (ROBIO) (pp. 467-472). IEEE.

[[21](https://ieeexplore.ieee.org/stamp/stamp.jsp?arnumber=9216032)] Yang, G., & Saniie, J. (2020). Sight-to-sound human-machine interface for guiding and navigating visually impaired people. IEEE Access, 8, 185416-185428.

[[22](https://link.springer.com/chapter/10.1007/978-3-642-23768-3_88)] Zöllner, M., Huber, S., Jetter, H. C., & Reiterer, H. (2011). NAVI–a proof-of-concept of a mobile navigational aid for visually impaired based on the microsoft kinect. In Human-Computer Interaction–INTERACT 2011: 13th IFIP TC 13 International Conference, Lisbon, Portugal, September 5-9, 2011, Proceedings, Part IV 13 (pp. 584-587). Springer Berlin Heidelberg.

[[23](https://www.researchgate.net/publication/257736351_Navigation_and_space_perception_assistance_for_the_visually_impaired_The_NAVIG_project)] Kammoun, S., Parseihian, G., Gutierrez, O., Brilhault, A., Serpa, A., Raynal, M., ... & Jouffrais, C. (2012). Navigation and space perception assistance for the visually impaired: The NAVIG project. Irbm, 33(2), 182-189.

[[24](https://www.mdpi.com/2079-9292/8/6/697)] Bai, J., Liu, Z., Lin, Y., Li, Y., Lian, S., & Liu, D. (2019). Wearable travel aid for environment perception and navigation of visually impaired people. Electronics, 8(6), 697.

[[25](https://pubmed.ncbi.nlm.nih.gov/30774566/)] Li, B., Munoz, J. P., Rong, X., Chen, Q., Xiao, J., Tian, Y., ... & Yousuf, M. (2018). Vision-based mobile indoor assistive navigation aid for blind people. IEEE transactions on mobile computing, 18(3), 702-714.

[[26](https://hal.science/hal-03351798/document)] Gay, S. L., Pissaloux, E., Romeo, K., & Truong, N. T. (2021). F2T: a novel force-feedback haptic architecture delivering 2D data to visually impaired people. IEEE Access, 9, 94901-94911.

[[27](https://arxiv.org/abs/2201.04453)] Zahn, M., & Khan, A. A. (2022). Obstacle avoidance for blind people using a 3D camera and a haptic feedback sleeve. arXiv preprint arXiv:2201.04453.

[[28](https://journals.sagepub.com/doi/10.1177/0145482X0309701007)] Zelek, J. S., Bromley, S., Asmar, D., & Thompson, D. (2003). A haptic glove as a tactile-vision sensory substitution for wayfinding. Journal of Visual Impairment & Blindness, 97(10), 621-632.

[[29](https://dl.acm.org/doi/abs/10.1145/2049536.2049628)] Shrewsbury, B. T. (2011, October). Providing haptic feedback using the kinect. In The proceedings of the 13th international ACM SIGACCESS conference on Computers and accessibility (pp. 321-322).

[[30](https://dl.acm.org/doi/10.1145/2513383.2513423)] Shen, H., Edwards, O., Miele, J., & Coughlan, J. M. (2013, October). CamIO: a 3D computer vision system enabling audio/haptic interaction with physical objects by blind users. In Proceedings of the 15th International ACM SIGACCESS Conference on Computers and Accessibility (pp. 1-2).

[[31](https://www.sciencedirect.com/science/article/pii/S0167865519300881)] Bauer, Z., Dominguez, A., Cruz, E., Gomez-Donoso, F., Orts-Escolano, S., & Cazorla, M. (2020). Enhancing perception for the visually impaired with deep learning techniques and low-cost wearable sensors. Pattern recognition letters, 137, 27-36.

[[32](https://www.researchgate.net/publication/264192906_A_Kinect_based_Vibrotactile_Feedback_System_to_Assist_the_Visually_Impaired)] Yelamarthi, K., DeJong, B. P., & Laubhan, K. (2014, August). A kinect based vibrotactile feedback system to assist the visually impaired. In 2014 IEEE 57th International Midwest Symposium on Circuits and Systems (MWSCAS) (pp. 635-638). IEEE.

[[33](https://pubmed.ncbi.nlm.nih.gov/2026426/)] Kaczmarek, K. A., Webster, J. G., Bach-y-Rita, P., & Tompkins, W. J. (1991). Electrotactile and vibrotactile displays for sensory substitution systems. IEEE transactions on biomedical engineering, 38(1), 1-16.

[[34](https://pdfs.semanticscholar.org/06c1/926b0c793d6be8537534c48518e40fc2cb58.pdf)] Ribani, R., & Marengoni, M. (2019, January). Vision Substitution with Object Detection and Vibrotactile Stimulus. In VISIGRAPP (4: VISAPP) (pp. 584-590).

[[35](https://pubmed.ncbi.nlm.nih.gov/14643370/)] Bach-y-Rita, P., & Kercel, S. W. (2003). Sensory substitution and the human–machine interface. Trends in cognitive sciences, 7(12), 541-546.

[[36](https://pubmed.ncbi.nlm.nih.gov/30440276/)] Mante, N., & Weiland, J. D. (2018, July). Visually impaired users can locate and grasp objects under the guidance of computer vision and non-visual feedback. In 2018 40th Annual International Conference of the IEEE Engineering in Medicine and Biology Society (EMBC) (pp. 1-4). IEEE.

[[37](https://www.researchgate.net/publication/224586228_Vibrotactile_feedback_systems_Current_trends_in_rehabilitation_sports_and_information_display)] Alahakone, A. U., & Senanayake, S. A. (2009, July). Vibrotactile feedback systems: Current trends in rehabilitation, sports and information display. In 2009 IEEE/ASME International Conference on Advanced Intelligent Mechatronics (pp. 1148-1153). IEEE.

[[38](https://www.researchgate.net/publication/355410847_Vibrotactile_Data_Physicalization_Exploratory_Insights_for_Haptization_of_Low-resolution_Images)] Bastidas Cuya, F. G., Martins Guarese, R. L., Johansson, C. G., Giambastiani, M., Iquiapaza, Y., de Jesus Oliveira, V. A., ... & Maciel, A. (2021, October). Vibrotactile Data Physicalization: Exploratory Insights for Haptization of Low-resolution Images. In Symposium on Virtual and Augmented Reality (pp. 84-91).

[[39](https://huggingface.co/Intel/dpt-large)] Intel DPT-Large Mono depth estimator

[[40](https://www.autodesk.com/products/eagle/features)] Eagle EDA

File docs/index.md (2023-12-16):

# Abstract

A Haptic feedback glove device that uses a motor camera and mini motor disks to help visually impaired people understand the 3d space around them. A small camera is mounted on the palm of a visually impaired user and is used to construct a depth map used to perform sensory substituition of vision using a high resolution haptic feedback device comprised of an array of mini DC motor discs with intensity analogous to how close an object is. The goal is for the user to be able to do wayfinding and navigate in a room using the device. User studies that examine the usability and quality of the device were done showing that the glove is easy to use, feels intuitive and engaging and is a suitable technique for sensory substitution of vision but was prone to errors, was not efficient and would not be recommended in the current stage to be used as a complete wayfinding solution.

# Team

* Theodoros Papaiakovou \#1 
* Fatemeh Arkannezhad \#2

# Required Submissions

* [Proposal](proposal.md)
* [Midterm Checkpoint Presentation Slides](https://drive.google.com/file/d/1Bj9LehYElW-KokTvbL8jPNXdkbFMn_he/view?usp=sharing)
* [Final Presentation Slides]([http://](https://docs.google.com/presentation/d/1Fas1VXkPGq1kGz_0-GN0VJX3lXwz_5BPYof5msbfPHM/edit?usp=sharing)https://docs.google.com/presentation/d/1Fas1VXkPGq1kGz_0-GN0VJX3lXwz_5BPYof5msbfPHM/edit?usp=sharing)
* [Final Report](report.md)

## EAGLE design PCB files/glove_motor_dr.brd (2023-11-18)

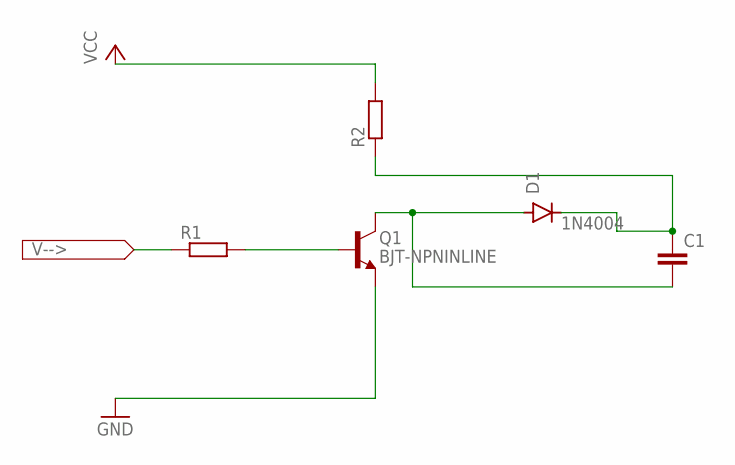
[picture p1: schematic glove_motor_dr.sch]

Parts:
C1: C-EU025-024X044; C025-024X044
D1: 1N4004; DO41-10
Q1: BJT-NPNINLINE; TO92I
R1, R2: R-EU_0207/7; 0207/7

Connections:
GND: Q1.E
MOTOR: C1.2, D1.A, Q1.C
unnamed: C1.1, D1.C, R2.1
unnamed: Q1.B, R1.2
VCC: R2.2

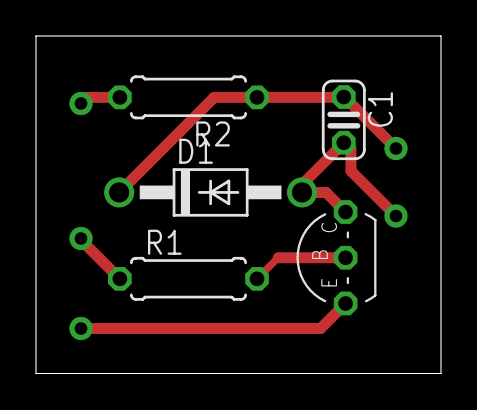
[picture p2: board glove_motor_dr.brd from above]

Board: 2 copper layers, 22.5 x 18.8 mm, 5 parts (0 on the bottom side), 3 nets.

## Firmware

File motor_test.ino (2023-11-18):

#include <HardwareSerial.h>

// Define motor pins
const int motorPins[] = {21, 19, 18, 5, 17, 16, 4, 22, 2, 15};

const int numMotors = sizeof(motorPins) / sizeof(motorPins[0]);
int motorIntensities[numMotors] = {0};

const byte maxDataSize = 2000;
char receivedData[maxDataSize];

void setup() {
  Serial.begin(9600);

  // Initiate motor GPIO pins as output
  for (int i = 0; i < sizeof(motorPins) / sizeof(motorPins[0]); i++) {
    pinMode(motorPins[i], OUTPUT);
  }
  // Output for LED pin that indicates status of serial communication
  pinMode(23,OUTPUT);
}

void loop() {
  
  
  if(Serial.available()){
    // Reads received serial message (expects a string of comma seperated values)
    char c;
    byte i = 0;
    while ((c = Serial.read()) != '\n' && i < maxDataSize - 1) {
      receivedData[i] = c;
      i++;
    }

    receivedData[i] = '\0';
    byte tokenCount = 0;

    // Splits the data at every comma
    char *token = strtok(receivedData, ",");
    while (token != NULL && tokenCount < numMotors) {
      int number = atoi(token);
      Serial.print("Received: ");
      Serial.print(number);
      // Assign the intensity to the motorIntensities array
      motorIntensities[tokenCount] = number;
      tokenCount++;
      token = strtok(NULL, ",");
    }

    // Serial.print(tokenCount);
    if (tokenCount != numMotors) {
      Serial.println("Error: Number of received numbers doesn't match the number of motors");
    }

    // light the LED to signify data reeception
    digitalWrite(23, 1);
    Serial.println("Intensities received");
  }
  
  // Assign PWM signal of received intensity based on the depth frame to each motor
  for (int i = 0; i < numMotors; i++) {
    analogWrite(motorPins[i], motorIntensities[i]);
    Serial.print(motorIntensities[i]);
  }
  // println is used ot sedn the previous serial messages back to Python backend for debugging
  Serial.println("Intensities");

  delay(50);
}

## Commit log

2023-10-16 Initial commit! Added depth_estimation.py a script that uses a depth transformer to find the depth of the images captured by laptops' camera Added calibrate_cam_script.py which can either use a folde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
2023-11-07 added close camera to depth_estimation.py Created depth_video_creating_script.py Created intensity_mapper.py Created serial_com.py Created main.py
2023-11-08 Update README.md
    Updated readme with hardware requirements and motor driver circuit details
2023-11-08 Added Arduino code
2023-11-08 PCB files
    Added schematic, board file as well as the cam files used to manufacture the PCBs of the motor drivers
    [glove_motor_dr.brd, glove_motor_dr.sch]
2023-12-16 experimented with depth_estimation.py Finished main.py which is the file to be execute to operate the prototype
